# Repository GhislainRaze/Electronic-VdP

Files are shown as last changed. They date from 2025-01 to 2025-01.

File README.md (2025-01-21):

# An electronic Van der Pol/Duffing oscillator

## Overview
This repository contains files for the realization of an electronic Van der Pol/Duffing oscillator, i.e., a circuit whose behavior is governed the equation

$\qquad m\ddot{x}(t) + (\mu x^2(t)+c)\dot{x}(t) + kx(t) + k_3 x^3(t) = f_{ext}(t),$
    
with $m>0$ and $k_3\geq0$.

The circuit takes a signal proportional to $f_{ext}$ and the parameters $c$ and $\mu$ as input and outputs signals proportional to $x$ and $\dot{x}$. It allows for tunable values of the parameters $k$ and $k_3$ via the use of potentiometers. It is also possible to chose positive or negative values for $k$ and obtain a single- or double-well oscillator, respectively.

The circuit requires an external power source with symmetric supplies. The input and output signals can be imposed/measured with BNC connectors.

## References

The circuit diagrams were realized using KiCad7.0 (https://www.kicad.org/), inspired from the following works:

\[1\] B. K. Jones and G. Trefan, “The Duffing oscillator: A precise electronic analog chaos demonstrator for the undergraduate laboratory,” Am. J. Phys., vol. 69, no. 4, pp. 464–469, Apr. 2001, doi: [10.1119/1.1336838](https://doi.org/10.1119/1.1336838).

\[2\] K. Srinivasan, K. Thamilmaran, and A. Venkatesan, “Effect of nonsinusoidal periodic forces in Duffing oscillator: Numerical and analog simulation studies,” Chaos, Solitons & Fractals, vol. 40, no. 1, pp. 319–330, Apr. 2009, doi: [10.1016/j.chaos.2007.07.090](https://doi.org/10.1016/j.chaos.2007.07.090).

## More information

For more infomation, see the [documentation file](DOC/Electronic_VdP.pdf).

## License

<p xmlns:cc="http://creativecommons.org/ns#" >This work is licensed under <a href="http://creativecommons.org/licenses/by/4.0/?ref=chooser-v1" target="_blank" rel="license noopener noreferrer" style="display:inline-block;">CC BY 4.0</a></p>

## See also

[An electronic Duffing oscillator](https://github.com/GhislainRaze/Electronic-Duffing)

## Disclaimer

It is believed by the author that the design does not violate the Copyright of any other party. This cannot be guaranteed however, and the author accepts no liability for loss or damages that may be imposed upon the user by any Court of Law, statutory or other body, should it transpire that a similar circuit has been simultaneously or previously designed, published or patented by another party.

The author cannot be held responsible for any issues or damages either to life or property, or as monetary or physical losses, that might occur during the use of this circuit, either due to negligence, ignorance or lack of proper knowledge about the subject. It is entirely the user’s responsibility to determine the suitability of this design for the intended purpose, and to take enough precautions before assembling and using the circuit.

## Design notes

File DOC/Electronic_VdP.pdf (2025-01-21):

## An electronic Van der Pol/Duffing oscillator

Ghislain Raze

November 2024 - Rev 1.0

## 1 General schematics of the electronic Van der Pol/Duffing oscillator

Figure 1 presents the (simplified) schematics of the electronic circuit used to implement a Van der Pol/Duffing oscillator in [1], inspired by [2–4]. The goal of this design was to create an oscillator with precisely tunable damping parameters. As shall be shown in Section 2, the relation between the input and output voltages, Vin and Vout, respectively, is a Van der Pol/Duffing equation. An additional output V1 is proportional to the time derivative of Vout. The circuit contains three operational amplifiers that make up two integrators and an inverting amplifier, two buffers, and five analog multipliers. Two potentiometers (p2 and p3) are used to tune some of the parameters of the circuit (the linear and cubic stiffness coefficients), while the remaining parameters (damping coefficients) are given by input signals to the circuit.

The practical realization in [1] also uses three additional switches and three additional buffers. The latter are needed to ensure low-impedance output and high-impedance input signals. As for the switches, two of them are used to enable the measurement of the division ratios of the potentiometers, and the third one can be used to obtain either a single- or double-well oscillator. Two additional potentiometers are also used to trim the offsets in the output signals. The circuit requires an external power source with symmetric supplies. The input and output signals can be imposed/measured with BNC connectors.

## 2 Governing equations

The following section assumes ideal operational amplifier behavior, i.e., no current flows into the input pins, and the voltage of these input pins is identical (due to the feedback action of the amplifier) [5]. It is also assumed that the buffers are perfect. Their output voltage is thus, from left to right, piVi (0 ≤ pi ≤ 1) for i = 2, 3, where p2 and p3 are the division ratios of the potentiometers.

Since the inverting input of the leftmost operational amplifier is (virtually) grounded, the currents going into R1, R2, R3, R4 and R8 all go into C1, summing up to I1. This realizes a summing integrator governed by

V˙
1 = −

1
C1

I1 = −

1
C1
p2V2
R2

+

p3V3
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
. | (1)

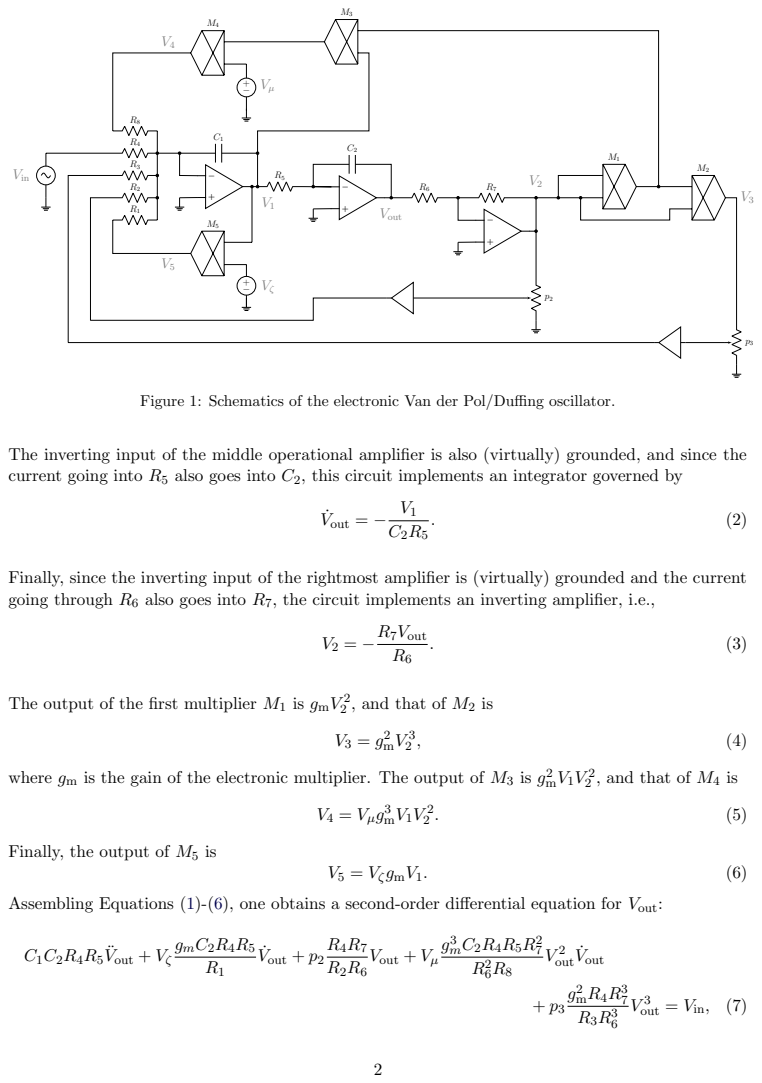
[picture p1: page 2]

Figure 1: Schematics of the electronic Van der Pol/Duffing oscillator.

The inverting input of the middle operational amplifier is also (virtually) grounded, and since the
current going into R5 also goes into C2, this circuit implements an integrator governed by

Finally, since the inverting input of the rightmost amplifier is (virtually) grounded and the current
going through R6 also goes into R7, the circuit implements an inverting amplifier, i.e.,

The output of the first multiplier M1 is gmV

2/2, and that of M2 is

2/2, and that of M4 is

where gm is the gain of the electronic multiplier. The output of M3 is g

Finally, the output of M5 is

Assembling Equations (1)-(6), one obtains a second-order differential equation for Vout:

which is a Van der Pol/Duffing equation of type

mV¨

out + cV˙
out + kVout + µV ²

outV˙
out + k3V

3
out = Vin. | (8)

Velocity signal

Forcing signal

Single/double-well switch

Power supply

Test points

Displacement
signal

Linear damping
coefficient

Nonlinear damping
coefficient

Displacement
offset

Velocity offset

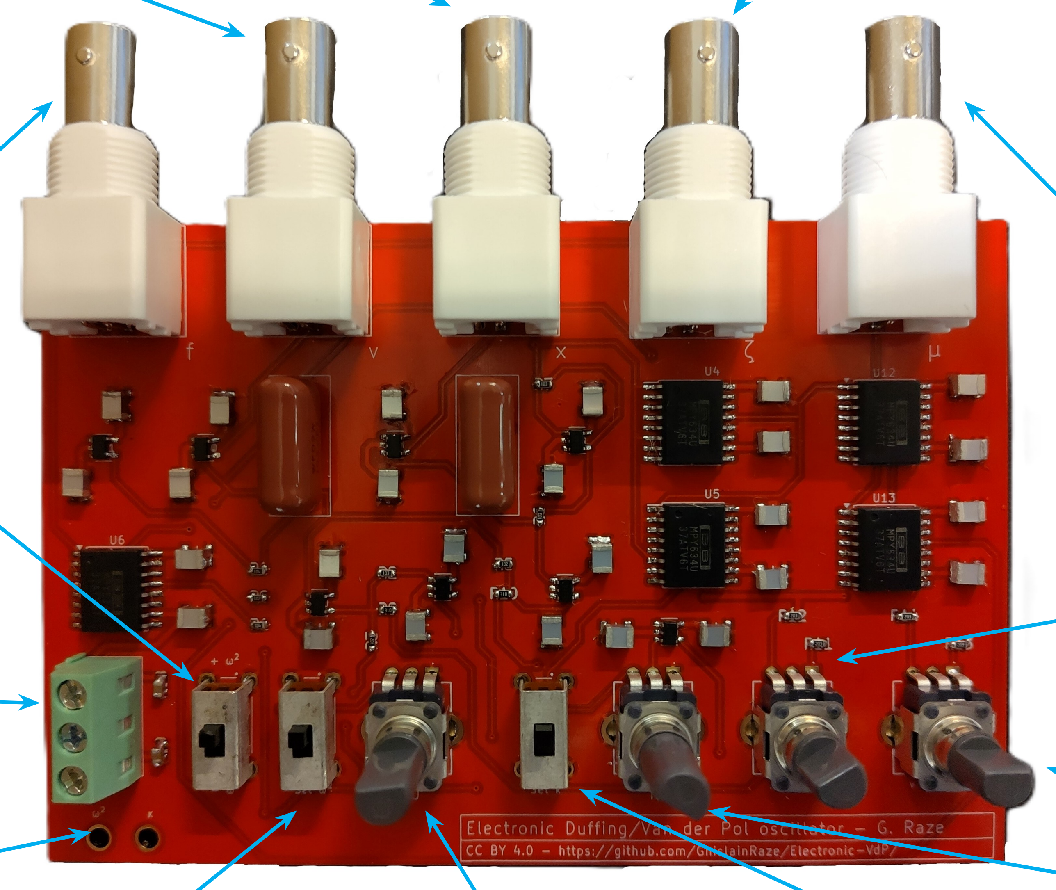
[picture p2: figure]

Frequency switch | Frequency knob | Nonlinear stiffenss switch

Nonlinear stiffness
knob

Figure 2: Picture of the electronic van der Pol/Duffing oscillator.

Figure 2 shows a photograph of the realization of the circuit in Figure 1 using Texas Instrument OPA210 operational amplifiers [6] and MPY634 multipliers [7].

## 3 Design choices

The electronic Van der Pol/Duffing oscillator was designed to be interfaced with a MicroLabBox from dSPACE, hence had to be able to work with voltages in the ±10 V range. These requirements guided the choice of the electrical parameters and integrated circuits, and are discussed in [4].

### 3.1 Integrated circuits choice

OPA210 are precision operational amplifiers with very low offset voltage (≤5 µV ), which was the main motivation for their selection, together with their supply voltage range (Vs = ±18 V ). In addition, they feature a large bandwidth for this application (GBW = 18 MHz) for a relatively low quiescent current [6]. For simplicity, buffers were realized with the same operational amplifiers in an input follower configuration.

The MPY634 analog multipliers were chosen for their availability, for their wide bandwidth (10 MHz) and for their adequate voltage range [7].

### 3.2 Other elements

Bipolar capacitors with high capacitances were needed to allow for relatively low resonance frequen-cies (in order to require reasonable resistances). Most dielectric materials with a high dielectric constant generally also feature high dissipation, which entails parasitic damping in the oscillator that can be complicated to model. Polypropylene (PP) film capacitors were thus selected for C1 and C2 due to their low dissipation, since their relatively large volume is not a problem in this application.

Lossy integrators can be used instead of the integrators implemented with the first and second operational amplifiers by placing a resistor with large resistance in parallel to C1 and/or C2. Since there was no saturation issue with the integrators, and since the offsets are quite small in the tested version of the circuit, this was not deemed necessary. In addition, this circuit contains potentiometers to trim the offsets.

Following the application note, bypass capacitors of 0.1µF were used for all integrated circuits [6], and bulk capacitors of 10µF were used for the power supply.

### 3.3 Parameter values

The design considerations outlined herein led to the parameters gathered in Table 1. Note that the potentiometers allow for a flexible range of parameters k and k3, but if the extreme values of these ranges are not satisfactory, other resistances and/or capacitances should be selected. The same goes for parameters c and µ.

Parameter | Value
R1 (kΩ) | 100
R2 (kΩ) | 10
R3 (kΩ) | 1
R4 (kΩ) | 100
R5 (kΩ) | 1
R6 (kΩ) | 10
R7 (kΩ) | 10
R8 (kΩ) | 1
C1 (µF) | 1
C2 (µF) | 1
gm (V⁻¹
) 0.1

Table 1: Electrical parameters of the electronic Van der Pol/Duffing oscillator.

## 4 Circuit implementation

### 4.1 Use of the circuit

The electrical Van der Pol/Duffing oscillator can be used in an experimental setup. This section briefly describes how to use the printed circuit board (PCB) in [1]. The reader can refer to Figure 2 to identify the different elements on the PCB.

BNC connectors are used to drive the circuit via the forcing signal port (symbol f on the PCB for Vin) and to measure its output (symbols x and v on the PCB for Vout and for V1, respectively). Additionally, the voltages Vζ and Vµ are set with BNC connectors (with symbols ζ and µ on the PCB, respectively), which allows for a precise tuning of the damping parameters. The circuit requires an external DC power source with symmetric supplies connected to the terminal block in the bottom left corner of the PCB. The supply voltage can range from ±8 V to ±18 V to comply with the maximum ratings of the integrated circuits [6, 7].

The parameters m, c, µ, k and k3 in Equation (8) can be computed by a simple comparison with Equation (7). The value of p2 and p3 can be adjusted by turning the knobs of the potentiometers. The switches Set ω

2 and Set κ on the PCB need to be up when the circuit is in operation, but can be down to make the determination of the value of these parameters easy when the circuit is not in operation. When they are down, they connect the potentiometers p2 and p3 (respectively) to the positive power supply. The output of the buffer connected to the potentiometer is also connected to a test point (vias) in the bottom left of the PCB (ω

2 and κ on the PCB, respectively). If the positive supply voltage is Vs and the switches are down, the voltage measured at these test points should be equal to piVs, allowing the user to deduce the value of pi

The last switch (±ω

2 on the PCB) is used to implement a single- or double-well oscillator, when the switch is up or down, respectively. In the latter case, p2 is connected to Vout instead of V2 (cf. Figure 1).

Finally, two potentiometers (x offset and v offset) can be adjusted to negate the DC voltage offsets of the x and v channels when there are no external forcing and limit cycles.

### 4.2 Non-ideal behavior

Although the circuit does replicate the dynamics of a Van der Pol/Duffing oscillator quite faithfully, this replication is not perfect due to several non-idealities. The ones suspected to be the most impactful are listed hereafter:

1. Voltage offsets: there exists voltage offsets at the input and output of the different integrated circuits, preventing a perfect symmetry in the oscillator. This can be partially fought with the trimming potentiometers. It is recommended to adjust them so as to have a zero output displacement and velocity when the input force is zero and there are no limit cycles.
2. Imperfect integrators: due to its finite open-loop gain, an operational amplifier used in an integrator will not perform an exact integration [6]. As also mentioned earlier, dissipation in the capacitors may also be the cause for an imperfect integrator behavior.
3. Imperfect nonlinearity: analog multipliers can also feature a small error (the output will not exactly be the product of the input voltages) [7].

## References

[1] G. Raze, “An electronic van der Pol/Duffing oscillator,” 2024. [Online]. Available: https://github.com/GhislainRaze/Electronic-VdP
[2] B. K. Jones and G. Trefan, “The Duffing oscillator: A precise electronic analog chaos demonstrator for the undergraduate laboratory,” Am. J. Phys., vol. 69, no. 4, pp. 464–469, apr 2001. [Online]. Available: https://pubs.aip.org/aapt/ajp/article/69/4/464-469/1055595
[3] K. Srinivasan, K. Thamilmaran, and A. Venkatesan, “Effect of nonsinusoidal periodic
forces in Duffing oscillator: | Numerical and analog simulation studies,” Chaos, Solitons
& Fractals, | vol. 40, | no. 1, | pp. 319–330, | apr 2009. [Online]. Available: | https:
//linkinghub.elsevier.com/retrieve/pii/S0960077907005796
[4] G. Raze, “An electronic Duffing oscillator,” 2024. [Online]. Available: https://github.com/GhislainRaze/Electronic-Duffing (https://github.com/GhislainRaze/Electronic-Duffing)
[5] P. Horowitz and W. Hill, The Art of Electronics, 3rd ed. Cambridge University Press, 2015.
[6] OPAx210 2.2-nV/√Hz Precision, Low-Power, 36-V Operational Amplifiers, Texas Instruments,

08 2021. [Online]. Available: https://www.ti.com/lit/ds/symlink/opa210.pdf

[7] Wide Bandwidth PRECISION ANALOG MULTIPLIER, Texas Instruments, 2004. [Online]. Available: https://www.ti.com/lit/ds/symlink/mpy634.pdf

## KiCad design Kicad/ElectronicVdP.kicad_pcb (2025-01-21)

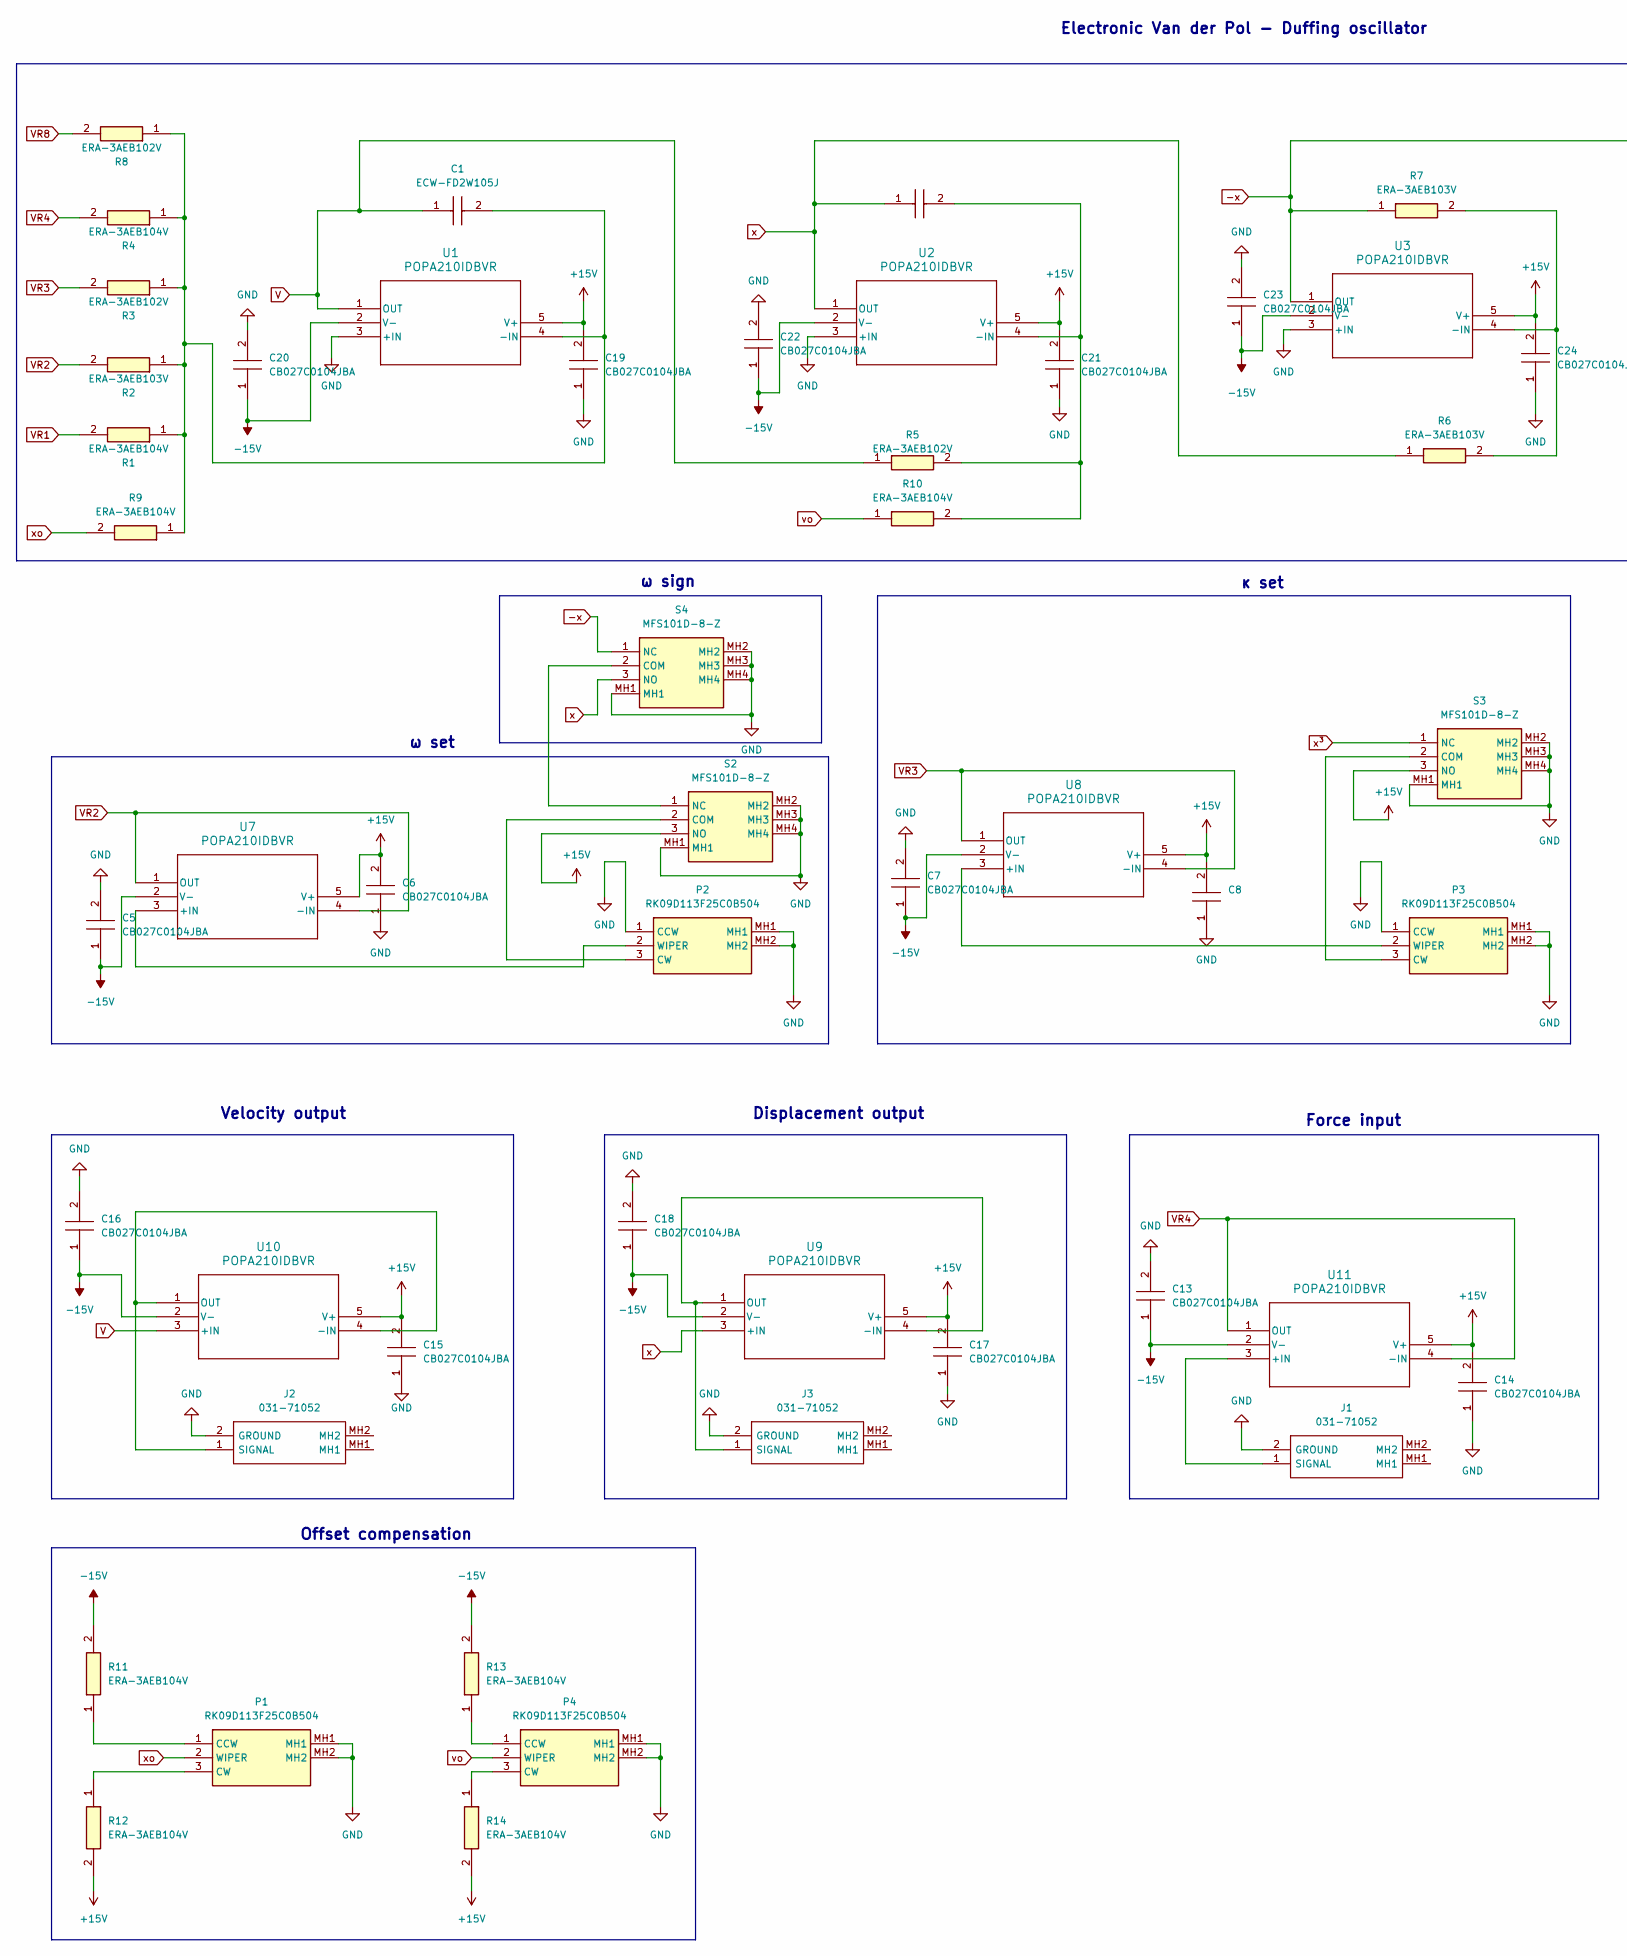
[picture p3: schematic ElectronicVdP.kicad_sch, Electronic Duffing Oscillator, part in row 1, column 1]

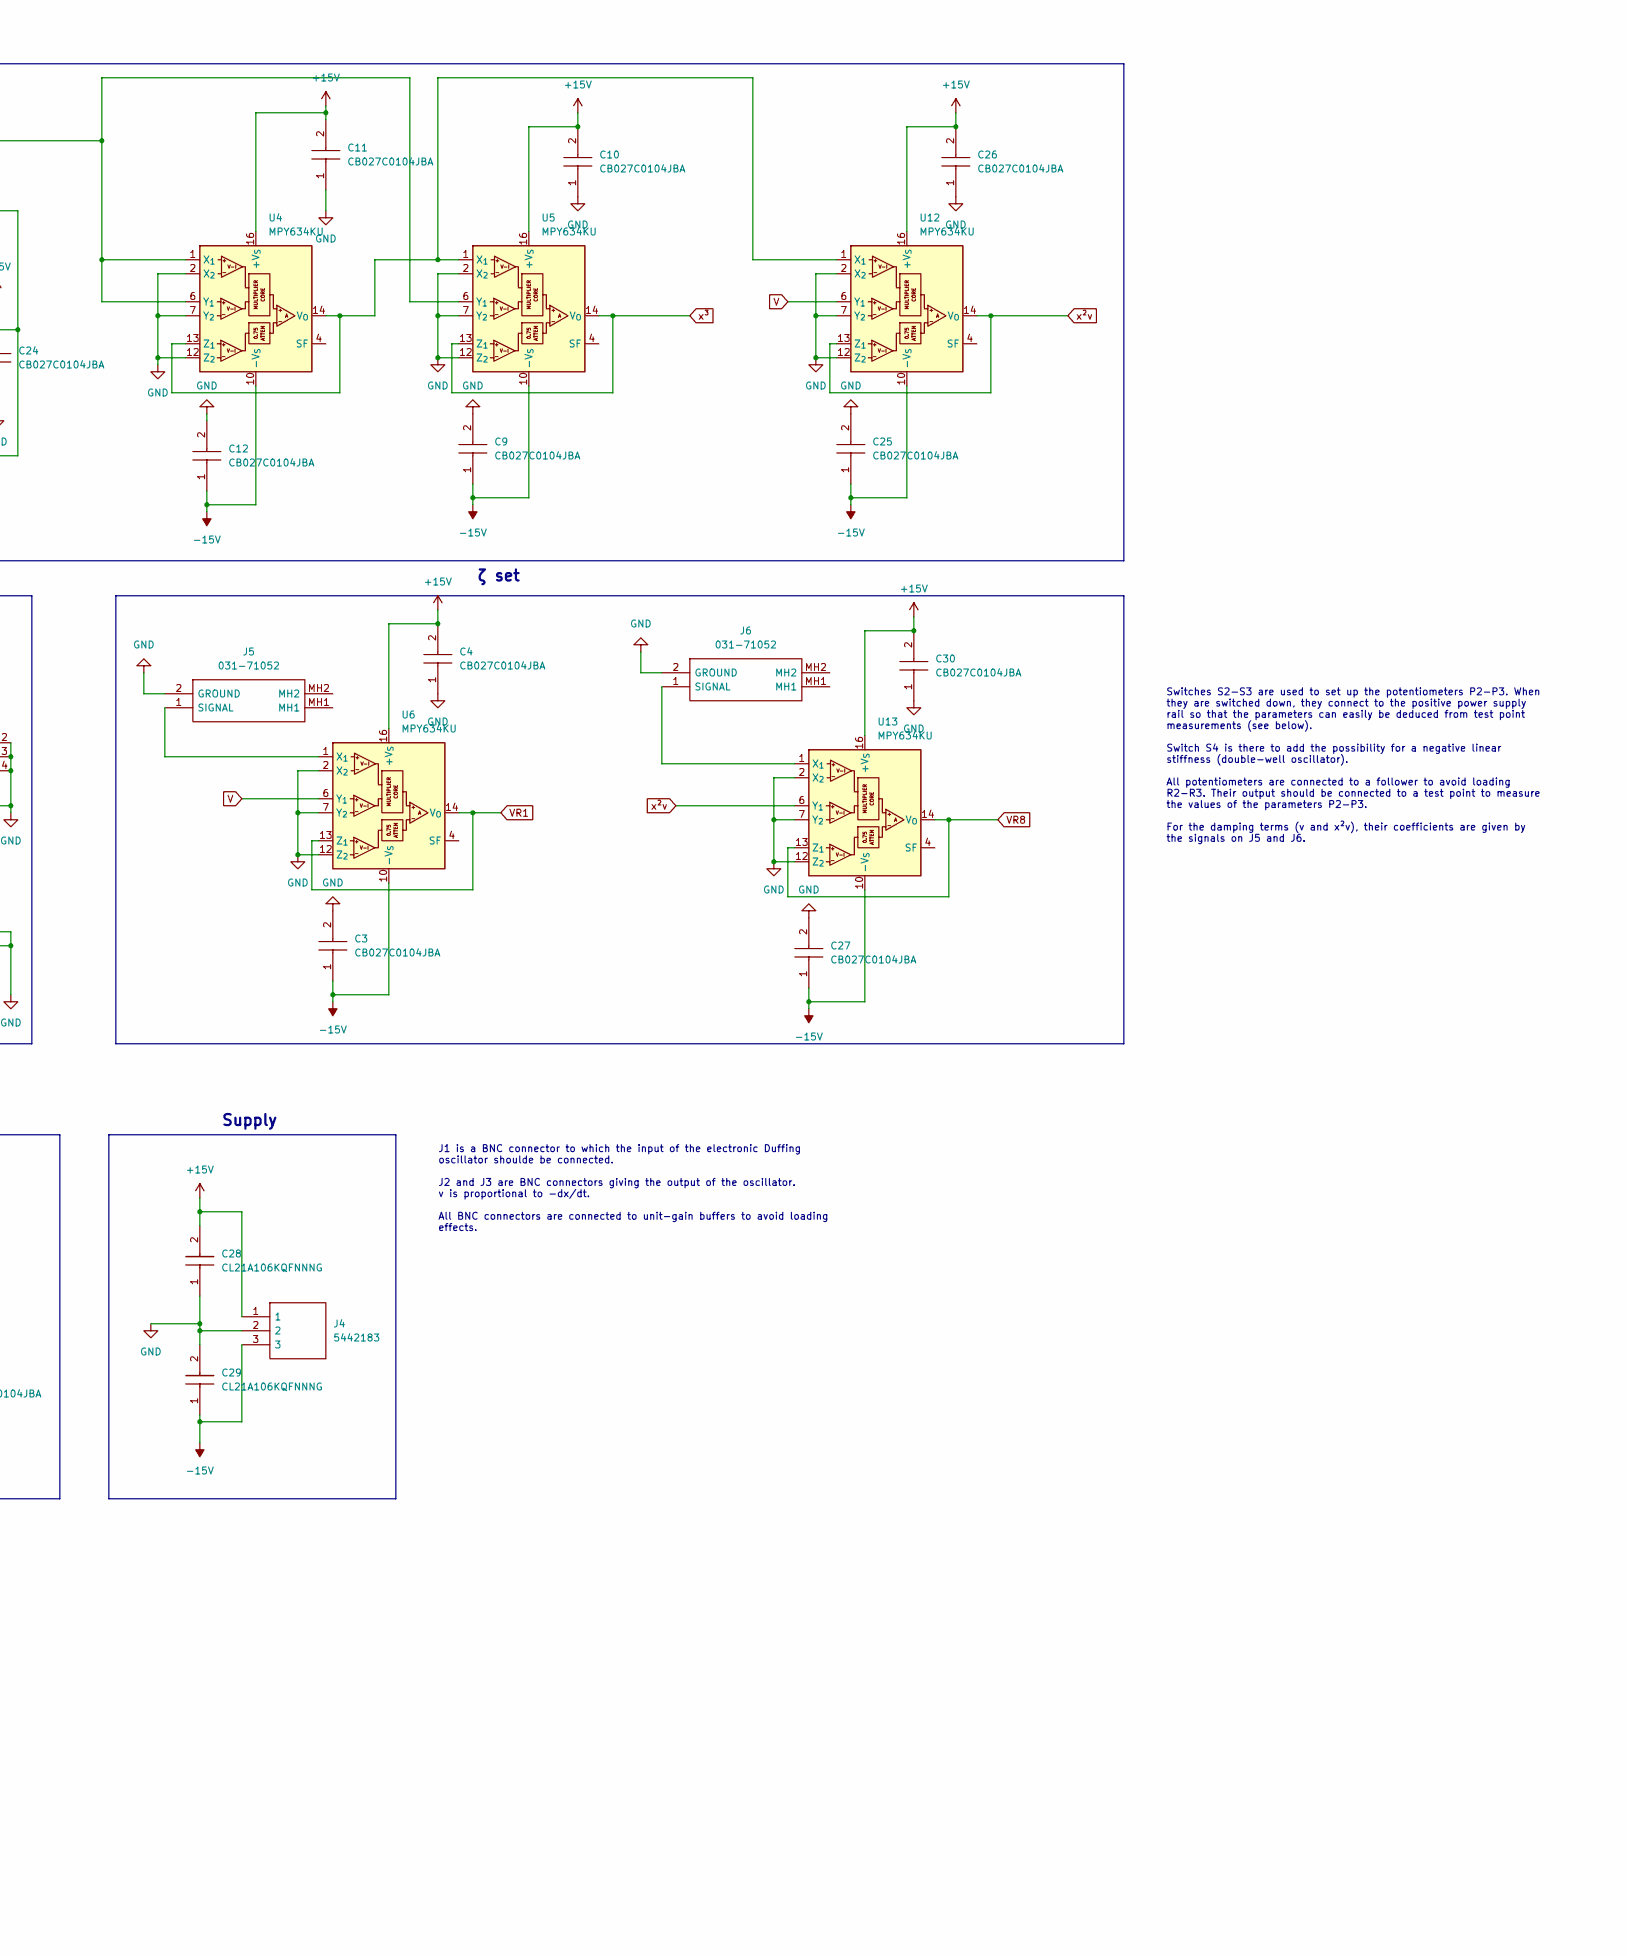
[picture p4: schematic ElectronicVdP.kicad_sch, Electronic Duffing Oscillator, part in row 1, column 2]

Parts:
C1, C2: ECW-FD2W105J; ECWFD2W105J; Mouser Part Number 667-ECW-FD2W105J
C3, C4, C5, C6, C7, C8, C9, C10, C11, C12, C13, C14, C15, C16, C17, C18, C19, C20, C21, C22, C23, C24, C25, C26, C27, C30: CB027C0104JBA; CAPC3325X230N; Mouser Part Number 581-CB027C0104JBA
C28, C29: CL21A106KQFNNNG; CAPC2012X135N; Mouser Part Number 187-CL21A106KQFNNNG
J1, J2, J3, J5, J6: 031-71052; 03171052; Manufacturer_Part_Number 031-71052
J4: 5442183; Mouser Part Number 651-5442183
P1, P2, P3, P4: RK09D113F25C0B504; Mouser Part Number 688-RK09D113F25-500K
R1, R4, R9, R10, R11, R12, R13, R14: ERA-3AEB104V; ERA3AEB101V; Mouser Part Number 667-ERA-3AEB104V
R2, R6, R7: ERA-3AEB103V; ERA3AEB101V; Mouser Part Number 667-ERA-3AEB103V
R3, R5, R8: ERA-3AEB102V; ERA3AEB101V; Mouser Part Number 667-ERA-3AEB102V
S2, S3, S4: MFS101D-8-Z; MFS101D8Z; Mouser Part Number 229-MFS101D-8-Z
U1, U2, U3, U7, U8, U9, U10, U11: POPA210IDBVR; SOT23_DBV_TEX
U4, U5, U6, U12, U13: MPY634KU; SOIC-16W_7.5x10.3mm_P1.27mm

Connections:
+15V: C4.2, C6.2, C8.2, C10.2, C11.2, C14.2, C15.2, C17.2, C19.2, C21.2, C24.2, C26.2, C28.2, C30.2, J4.1, R12.2, R14.2, S2.3 (NO), S3.3 (NO), U1.5 (V+), U2.5 (V+), U3.5 (V+), U4.16 (+V_{S}), U5.16 (+V_{S}), U6.16 (+V_{S}), U7.5 (V+), U8.5 (V+), U9.5 (V+), U10.5 (V+), U11.5 (V+), U12.16 (+V_{S}), U13.16 (+V_{S})
-15V: C3.1, C5.1, C7.1, C9.1, C12.1, C13.1, C16.1, C18.1, C20.1, C22.1, C23.1, C25.1, C27.1, C29.1, J4.3, R11.2, R13.2, U1.2 (V-), U2.2 (V-), U3.2 (V-), U4.10 (-V_{S}), U5.10 (-V_{S}), U6.10 (-V_{S}), U7.2 (V-), U8.2 (V-), U9.2 (V-), U10.2 (V-), U11.2 (V-), U12.10 (-V_{S}), U13.10 (-V_{S})
-x: R7.1, S4.1 (NC), U3.1 (OUT), U4.1 (X_{1}), U4.6 (Y_{1}), U5.6 (Y_{1})
GND: C3.2, C4.1, C5.2, C6.1, C7.2, C8.1, C9.2, C10.1, C11.1, C12.2, C13.2, C14.1, C15.1, C16.2, C17.1, C18.2, C19.1, C20.2, C21.1, C22.2, C23.2, C24.1, C25.2, C26.1, C27.2, C28.1, C29.2, C30.1, J1.2 (GROUND), J2.2 (GROUND), J3.2 (GROUND), J4.2, J5.2 (GROUND), J6.2 (GROUND), P1.MH1, P1.MH2, P2.1 (CCW), P2.MH1, P2.MH2, P3.1 (CCW), P3.MH1, P3.MH2, P4.MH1, P4.MH2, S2.MH1, S2.MH2, S2.MH3, S2.MH4, S3.MH1, S3.MH2, S3.MH3, S3.MH4, S4.MH1, S4.MH2, S4.MH3, S4.MH4, U1.3 (+IN), U2.3 (+IN), U3.3 (+IN), U4.2 (X_{2}), U4.7 (Y_{2}), U4.12 (Z_{2}), U5.2 (X_{2}), U5.7 (Y_{2}), U5.12 (Z_{2}), U6.2 (X_{2}), U6.7 (Y_{2}), U6.12 (Z_{2}), U12.2 (X_{2}), U12.7 (Y_{2}), U12.12 (Z_{2}), U13.2 (X_{2}), U13.7 (Y_{2}), U13.12 (Z_{2})
unnamed: J1.1 (SIGNAL), U11.3 (+IN)
unnamed: J2.1 (SIGNAL), U10.1 (OUT), U10.4 (-IN)
unnamed: J3.1 (SIGNAL), U9.1 (OUT), U9.4 (-IN)
unnamed: J5.1 (SIGNAL), U6.1 (X_{1})
unnamed: J6.1 (SIGNAL), U13.1 (X_{1})
unnamed: P1.1 (CCW), R11.1
unnamed: P1.3 (CW), R12.1
unnamed: P2.3 (CW), S2.2 (COM)
unnamed: P2.2 (WIPER), U7.3 (+IN)
unnamed: P3.3 (CW), S3.2 (COM)
unnamed: P3.2 (WIPER), U8.3 (+IN)
unnamed: P4.1 (CCW), R13.1
unnamed: P4.3 (CW), R14.1
unnamed: S2.1 (NC), S4.2 (COM)
unnamed: C1.2, R1.1, R2.1, R3.1, R4.1, R8.1, R9.1, U1.4 (-IN)
unnamed: C2.2, R5.2, R10.2, U2.4 (-IN)
unnamed: R6.2, R7.2, U3.4 (-IN)
unnamed: U4.13 (Z_{1}), U4.14 (V_{O}), U5.1 (X_{1}), U12.1 (X_{1})
V: C1.1, R5.1, U1.1 (OUT), U6.6 (Y_{1}), U10.3 (+IN), U12.6 (Y_{1})
VR1: R1.2, U6.13 (Z_{1}), U6.14 (V_{O})
VR2: R2.2, U7.1 (OUT), U7.4 (-IN)
VR3: R3.2, U8.1 (OUT), U8.4 (-IN)
VR4: R4.2, U11.1 (OUT), U11.4 (-IN)
VR8: R8.2, U13.13 (Z_{1}), U13.14 (V_{O})
vo: P4.2 (WIPER), R10.1
x: C2.1, R6.1, S4.3 (NO), U2.1 (OUT), U9.3 (+IN)
xo: P1.2 (WIPER), R9.2
x²v: U12.13 (Z_{1}), U12.14 (V_{O}), U13.6 (Y_{1})
x³: S3.1 (NC), U5.13 (Z_{1}), U5.14 (V_{O})

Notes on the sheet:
ω set
Offset compensation
κ set
ω sign
Force input
J1 is a BNC connector to which the input of the electronic Duffing oscillator shoulde be connected. J2 and J3 are BNC connectors giving the output of the oscillator. v is proportional to -dx/dt. All BNC connectors are connected to unit-gain buffers to avoid loading effects.
Switches S2-S3 are used to set up the potentiometers P2-P3. When they are switched down, they connect to the positive power supply rail so that the parameters can easily be deduced from test point measurements (see below). Switch S4 is there to add the possibility for a negative linear stiffness (d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
ζ set
Supply
Displacement output
Velocity output
Electronic Van der Pol - Duffing oscillator

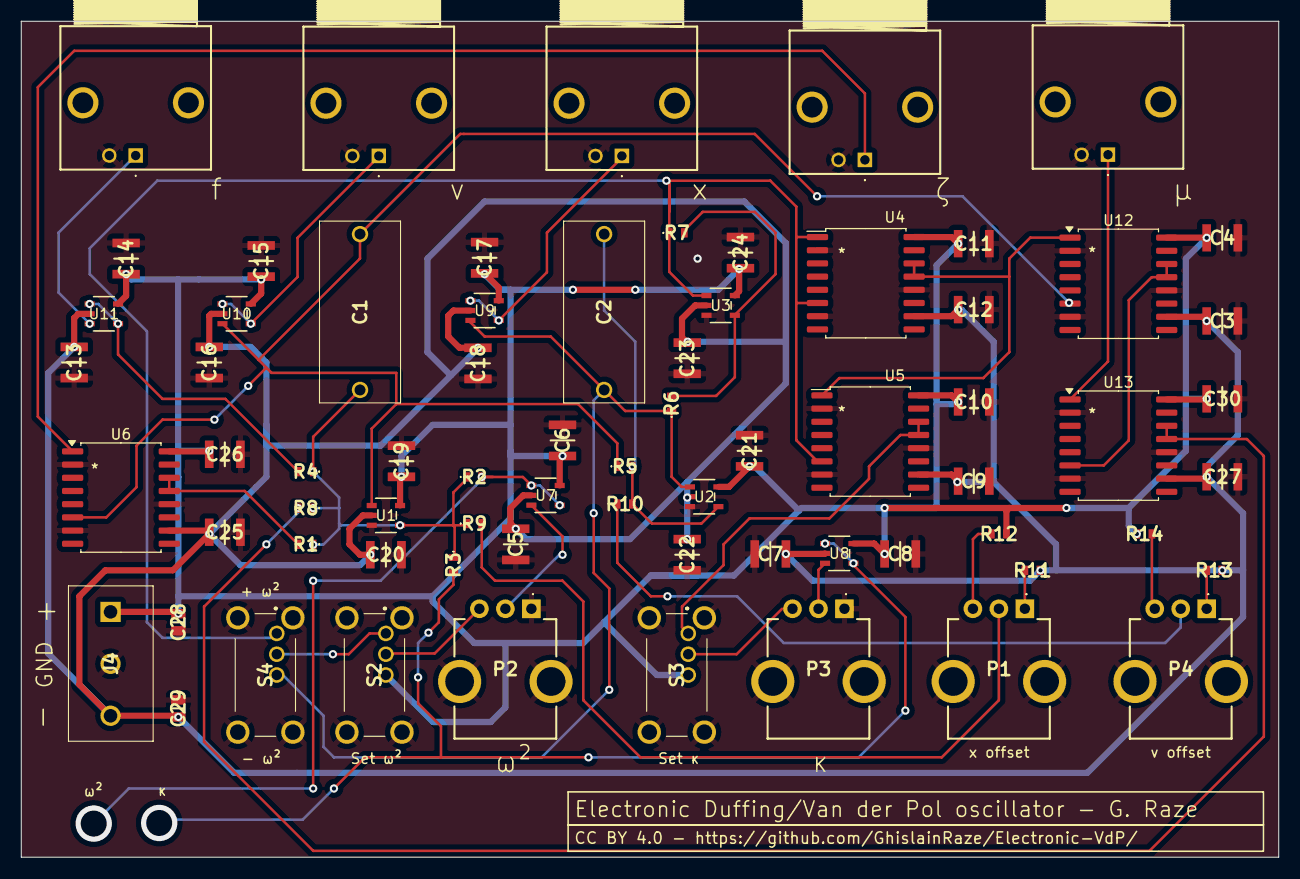
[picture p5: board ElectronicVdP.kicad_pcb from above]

Board: 2 copper layers, 121.0 x 80.5 mm, 70 parts (0 on the bottom side), 33 nets.

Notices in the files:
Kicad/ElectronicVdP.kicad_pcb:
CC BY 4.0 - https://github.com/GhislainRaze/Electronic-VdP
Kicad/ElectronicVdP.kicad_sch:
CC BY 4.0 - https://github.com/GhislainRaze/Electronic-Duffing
